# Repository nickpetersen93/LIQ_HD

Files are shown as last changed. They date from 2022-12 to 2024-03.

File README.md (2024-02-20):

# LIQ HD - Lick Instance Quantifier Home cage Device 

## UPDATE: 1/19/2024 (Arduino Mega version only)

We have now included the ability to log the lick data by individual bouts! With this setting turned on, each individual bout will be logged with a line in the file with the side the experimental bottle is on (LEFT or RIGHT), a time stamp, the cage number, which bottle was licked (LEFT or RIGHT), bout lick number, bout lick duration, average lick frequency of that bout, and average inter-lick interval of that bout. Note, this setting will not log the total lick number and lick duration (i.e. licks that do not meet bout criteria).

The "log by bout" setting can be turned on using the GUI under "Parameters to log". This setting can be made the default by changing the Arduino code lines 186-187. For example:

bool log_by_bout = true; 
bool log_by_time = false;
//will set the default to "log by bout".

bool log_by_bout = false; 
bool log_by_time = true;
//will set the default to "log by time" (original logging method).

We have also made it easier to change the bout cutoff time (the amount of time during a drinking bout where an animal stops licking before the bout is considered over) by changing the "bout_cutoff" variable on line 185.

We made some minor changes to the capacitive sensor settings that optimizes the baseline tracking for more consistent lick detection.

------------------------------------------------------------------

## Included in this repository:
  - Arduino code for LIQ HD running off an Arduino Mega
  - Arduino code for LIQ HD running off an Adafruit Grand Central (significantly faster processor speed. NOT FULLY TESTED.)
  - 3D models for all required 3D-printed components in various file formats (STL, STEP, SHAPR)
  - Step-by-step build instructions and video tutorial can be found on the [Wiki page](https://github.com/nickpetersen93/LIQ_HD/wiki/LIQ-HD---Step-by-Step-Tutorial "LIQ HD - Step-by-Step Tutorial")
  
------------------------------------------------------------------

### Required Arduino Libraries:
  - Adafruit_GFX.h
  - RTClib.h
  - SdFat.h
  - Adafruit_MPR121.h
  - Adafruit_ILI9341.h
  - Adafruit_FT6206.h
  
------------------------------------------------------------------

### Publication Link: https://www.eneuro.org/content/10/4/ENEURO.0506-22.2023

## Abstract

Investigation of rodent drinking behavior has provided insight into drivers of thirst, circadian rhythms, anhedonia, and drug and ethanol consumption. Traditional methods of recording fluid intake involve periodically weighing bottles, which is cumbersome and lacks temporal resolution. Several open-source devices have been designed to improve drink monitoring, particularly for two-bottle choice tasks. However, recent designs are limited by the use of infrared photobeam-break sensors and incompatibility with prolonged undisturbed use in ventilated home cages. Beam-break sensors lack accuracy for bout microstructure analysis and are prone to damage from rodents. To address these concerns, we designed LIQ HD (Lick Instance Quantifier Home cage Device) with the goal of utilizing capacitive sensors to increase accuracy and analyze lick microstructure, building a device compatible with ventilated vivarium home cages, increasing scale with prolonged undisturbed recordings, and creating a design that is easy to build and use with an intuitive touchscreen graphical user interface. The system tracks two-bottle choice licking behavior in up to 18 rodent home cages, or 36 single bottles, on a minute-to-minute timescale controlled by a single Arduino microcontroller. The data are logged to a single SD card, allowing for efficient downstream analysis. With sucrose, quinine, and ethanol two-bottle choice tasks, we validated that LIQ HD has superior accuracy compared to beam-break sensors. The system measures preference over time and changes in bout microstructure, with undisturbed recordings lasting up to 7 days. All designs and software are open-source to allow other researchers to build upon the system and adapt LIQ HD to their animal home cages.

<p align="center">

</p>

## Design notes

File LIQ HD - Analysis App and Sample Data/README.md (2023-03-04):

# LIQ HD Analysis 

<p align="center">
LIQ HD Analysis App
</p>

## Included in this folder:
  - LIQ HD Analysis 1.0 Installer for MacOS and Windows
  - Sample LIQ HD Data
    - "LIQ_HD_Sample_Data_Water.CSV" contains data from 16 cages of water two-bottle choice for 1 week. Cages 17 & 18 are empty.
    - "LIQ_HD_Sample_Data_EtOH_Sucrose.CSV" contains data from 8 cages of ethanol two-bottle choice (Cages 1 to 8 - 7% EtOH versus water), and 8 cages of sucrose two-bottle choice (Cages 9 to 16 - 1% Sucrose versus water) for 1 week. Cages 17 & 18 are empty.
  - A How-To Guide can be found on the [Wiki page](https://github.com/nickpetersen93/LIQ_HD/wiki/LIQ-HD-Analysis-App-Guide) (Coming soon!)

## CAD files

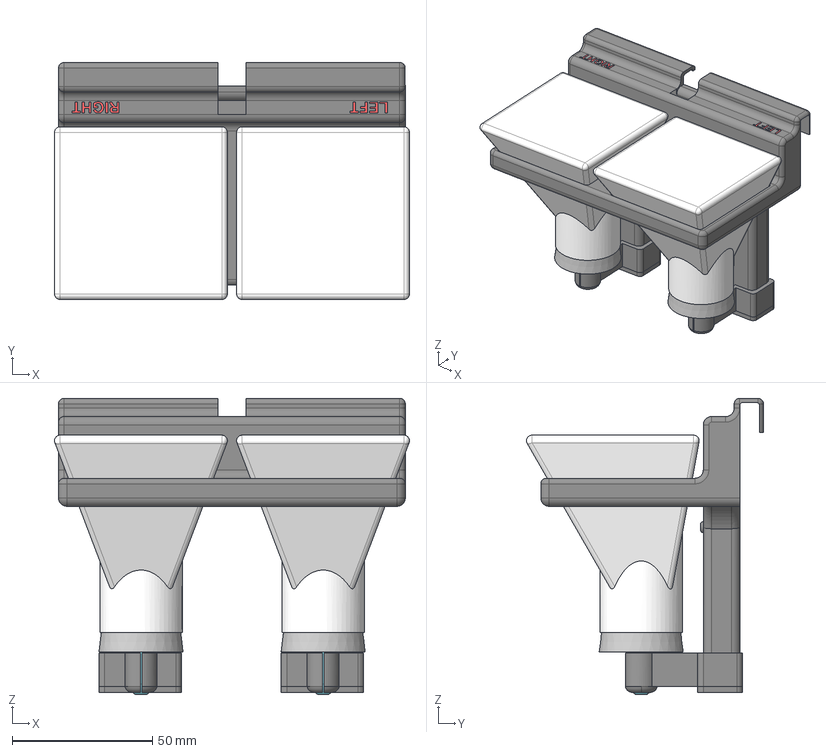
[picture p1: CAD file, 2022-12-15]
LIQ HD - 3D Models github/STEP/LIQ HD - Full model.step
126.5 x 84.5 x 105.6 mm
spouts
stoppers
clips
Text - LEFT/RIGHT
bottles

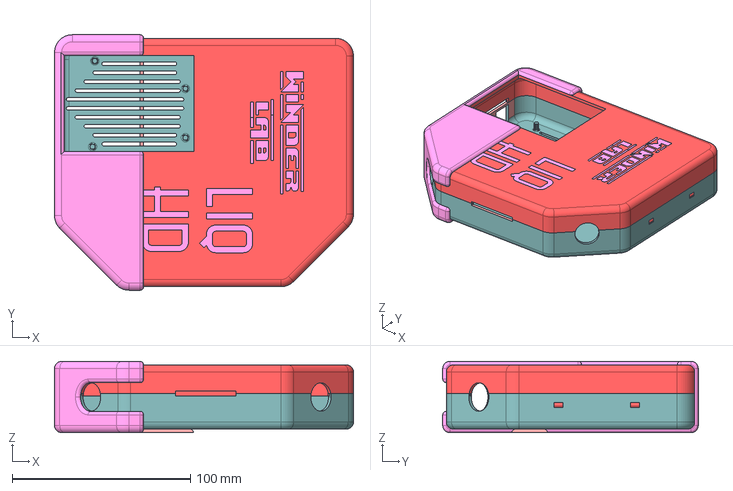
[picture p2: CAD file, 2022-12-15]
LIQ HD - 3D Models github/STEP/LIQ HD - Arduino Box.step
167.8 x 143.4 x 40.0 mm

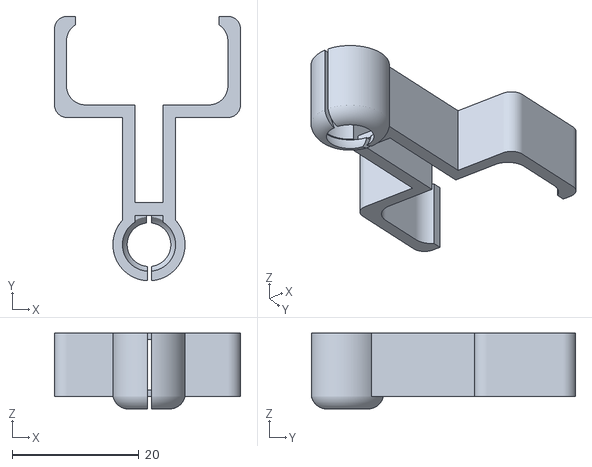
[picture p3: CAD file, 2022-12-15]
LIQ HD - 3D Models github/STL/LIQ HD - Device CLIP 10mm.stl
29.4 x 41.8 x 12.0

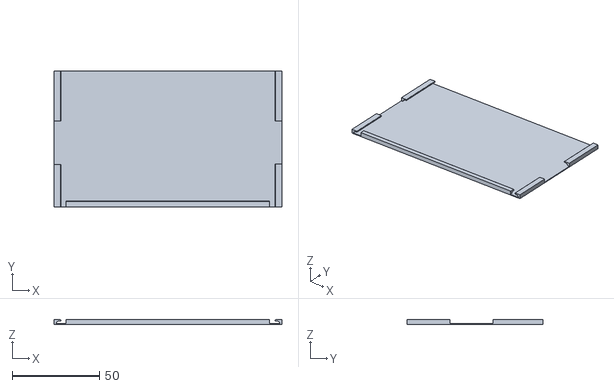
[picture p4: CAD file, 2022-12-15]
LIQ HD - 3D Models github/STL/LIQ HD Card Holder.stl
131.0 x 78.0 x 2.80

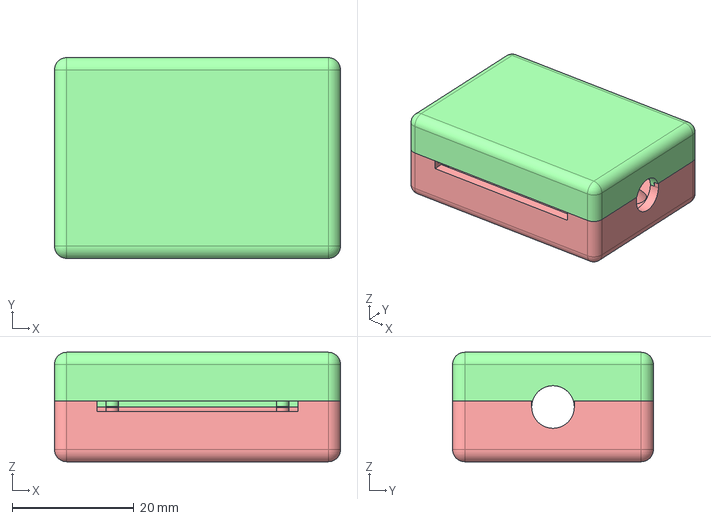
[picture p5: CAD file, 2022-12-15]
LIQ HD - 3D Models github/STEP/LIQ HD - Sensor Box.step
47.0 x 33.0 x 18.0 mm

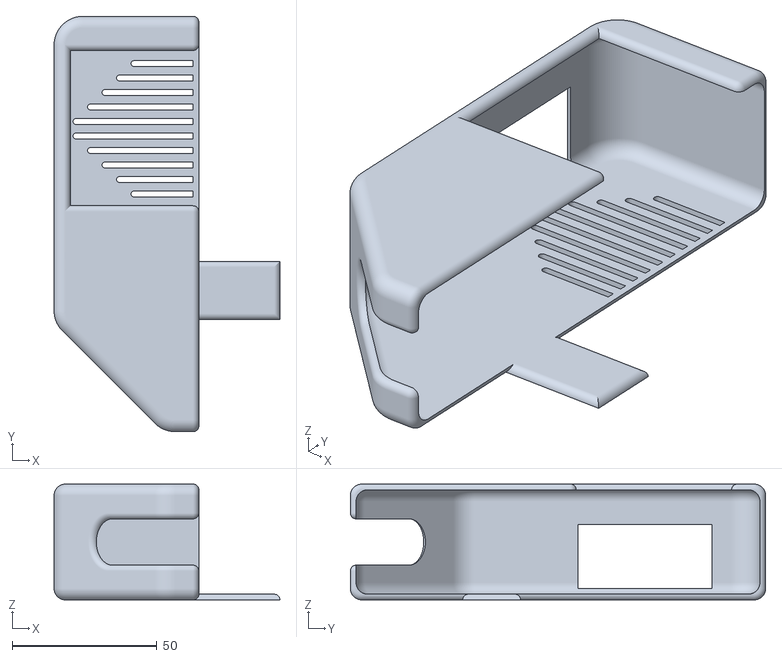
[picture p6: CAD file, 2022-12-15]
LIQ HD - 3D Models github/STL/LIQ HD - Arduino box HOLDER.stl
78.0 x 143.4 x 40.0

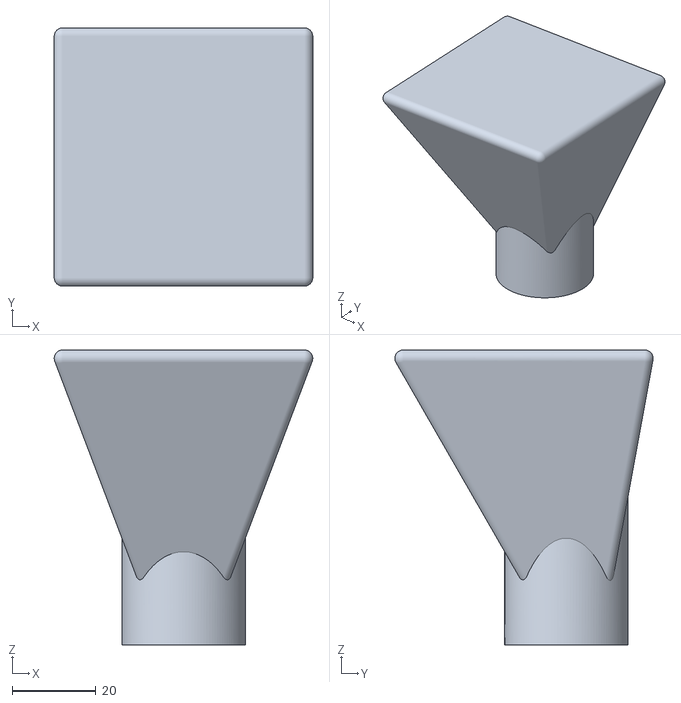
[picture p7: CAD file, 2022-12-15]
LIQ HD - 3D Models github/STL/LIQ HD - Bottle 27mm opening.stl
61.6 x 61.5 x 70.3

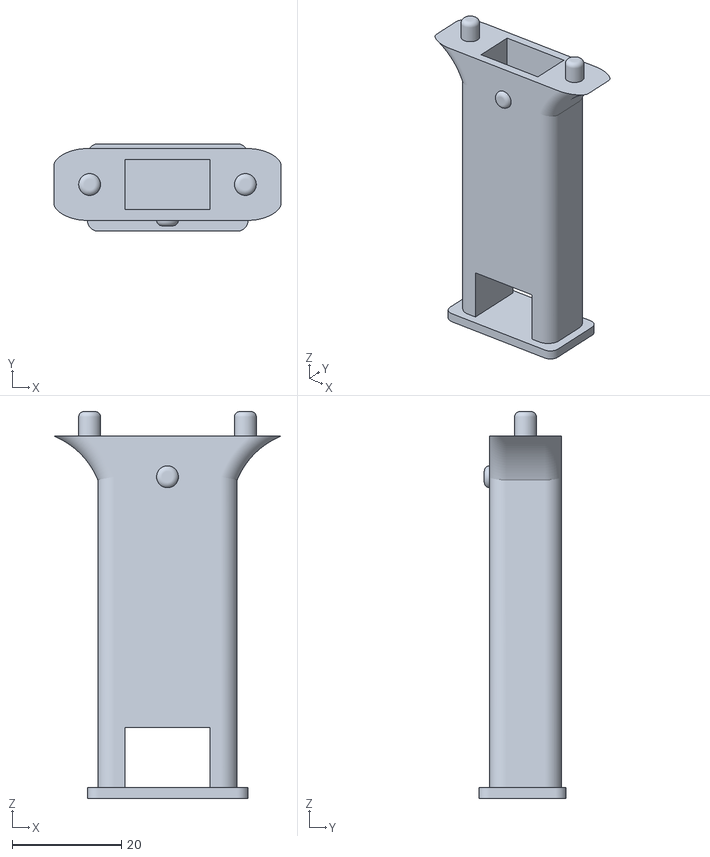
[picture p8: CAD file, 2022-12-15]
LIQ HD - 3D Models github/STL/LIQ HD - Device LEG .stl
41.5 x 16.0 x 70.8

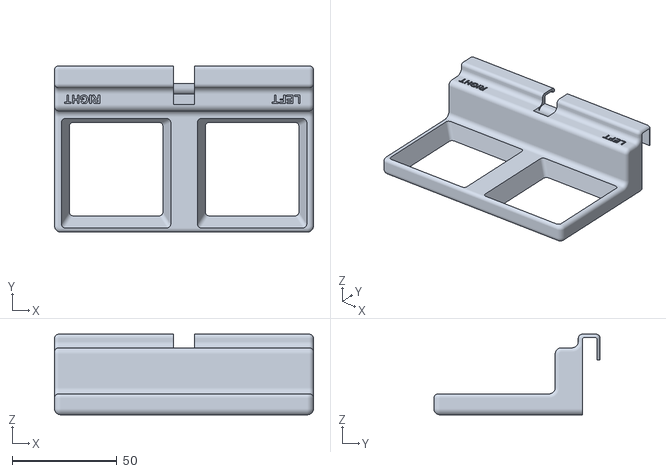
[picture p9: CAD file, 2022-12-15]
LIQ HD - 3D Models github/STL/LIQ HD - Device TOP.stl
123.6 x 79.4 x 38.5

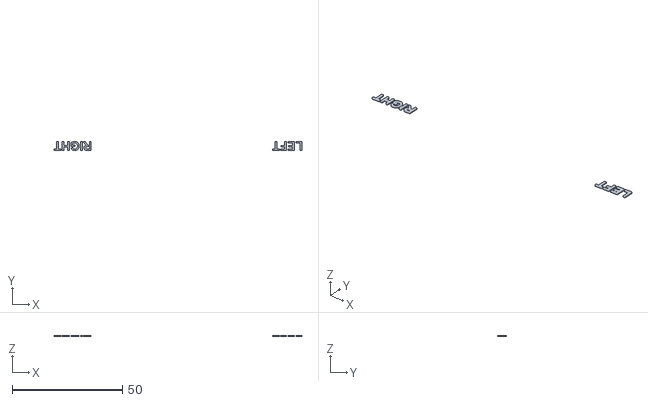
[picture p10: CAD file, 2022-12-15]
LIQ HD - 3D Models github/STL/LIQ HD - Device TEXT.stl
112.5 x 4.14 x 0.6

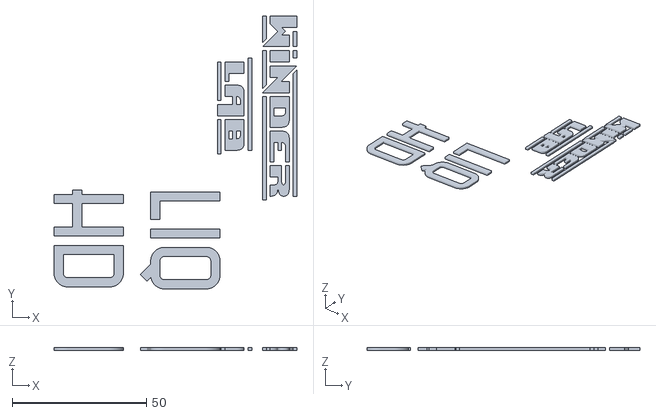
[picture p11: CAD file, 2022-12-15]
LIQ HD - 3D Models github/STL/LIQ HD - Arduino box TEXT.stl
90.5 x 101.6 x 1.00

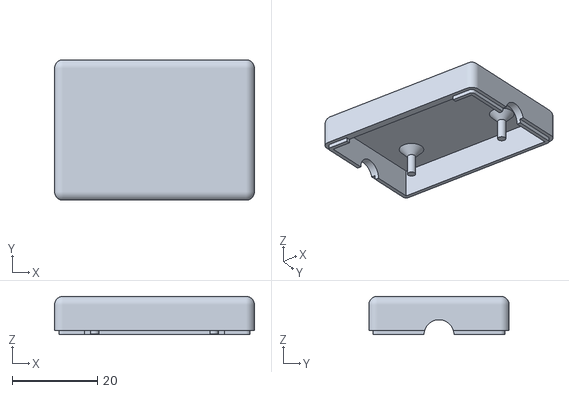
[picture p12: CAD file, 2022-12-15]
LIQ HD - 3D Models github/STL/LIQ HD - Sensor case TOP.stl
47.0 x 33.0 x 9.00

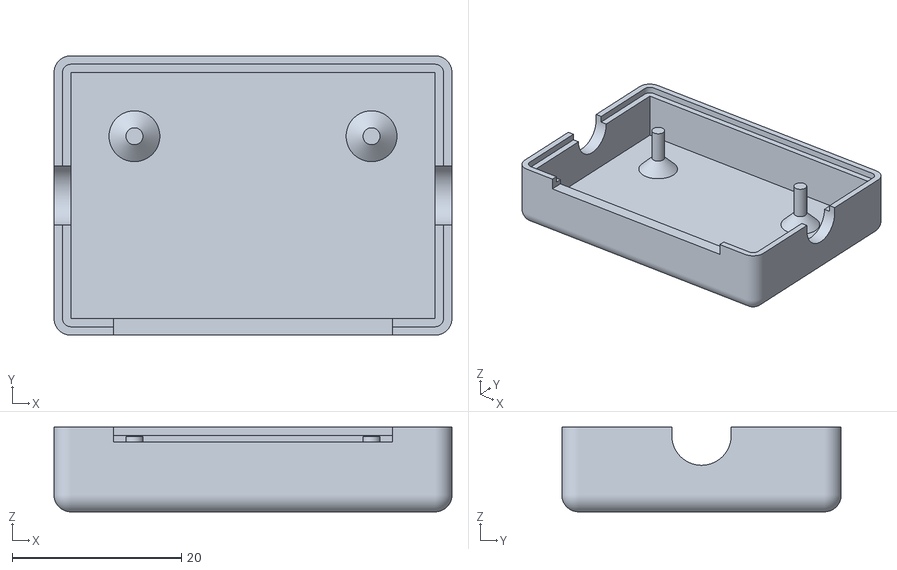
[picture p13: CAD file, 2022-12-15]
LIQ HD - 3D Models github/STL/LIQ HD - Sensor case BOTTOM.stl
47.0 x 33.0 x 10.0

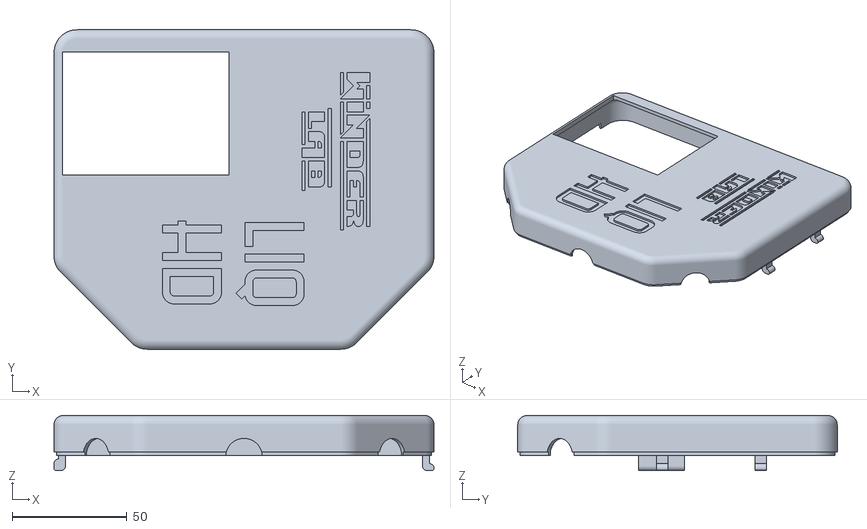
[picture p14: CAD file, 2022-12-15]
LIQ HD - 3D Models github/STL/LIQ HD - Arduino box TOP.stl
165.8 x 139.4 x 24.0

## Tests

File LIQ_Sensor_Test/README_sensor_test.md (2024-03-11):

Upload this script to your LIQ HD system and open the serial plotter on the Arduino IDE to visually test lick threshold settings! It is recomended to test only 2-4 sensors because the serial plotter begins to run slowly. If the serial plotter is running too quickly to visualize detected licks, you can slow it down by adding a delay (change "delay_time"). Run this test on a fully built LIQ system in its experimental environment because certain changes, such as wire length, will affect the necessary threshold settings.

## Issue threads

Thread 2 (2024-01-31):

### ISSUE TITLE
STL Files provided don't match with video

### ISSUE THREAD

**Issue by IamMistborn** [nickpetersen93/LIQ_HD#2]
Hey there, I was going through the tutorial when I realized the Youtube video STL files and the STL files provided on Thingiverse don't match up. What's more, it looks like the STL files have additional hardware that isn't mentioned in the video, Step-By-Step tutorial, or materials list. I'm mostly wondering if I'm missing something crucial that was added later on. Thanks!

**Comment by nickpetersen93** [comment]
Hello! We have not uploaded anything to Thingiverse, but it looks like there is a modified version that was adapted from our system made by another lab [(link)](https://www.thingiverse.com/thing:6301818). From what I can tell from their design, the general build of the electronic components in the same, but with a modified in-cage sipper sensor to fit their cages.

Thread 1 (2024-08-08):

### ISSUE TITLE
Time resolution of data aggregation

### ISSUE THREAD

**Issue by shun4423** [nickpetersen93/LIQ_HD#1]
This system seems to summarize data as licks per minute, but is it possible to summarize data as licks per second?

**Comment by nickpetersen93** [comment]
Theoretically, yes, the code can be modified to log every second, but I don’t think it would be helpful. It takes time to write to the file and save to the SD card, so this would probably cause significant lapses in the lick detection. Is there a specific reason you’d like to log every second? We are currently working on updating the code to include an option to log every drinking bout rather than logging every ‘x’ minutes. This will decrease the file size and also allow for very specific analysis of each bout. We are also fine-tuning the lick detection settings to further increase the accuracy. This should be released in the next few weeks!

**Comment by shun4423** [comment]
Where a licked clump is considered terminated varies. In my case, the end of a bout is when there is no lick for one second after consecutive licks. I also calculate the interval between boats. Therefore, I fear that if I compile the data in one-minute increments, I will not be able to calculate these.

**Comment by Zepieton** [comment]
We have a built a Liq HD system and it seems to work fine so far; but we want to to be able to use each lick bout as a TTL to time-lock them to specific events (brain recordings). Any way to achieve this with the current code? Or is it going to be in the updated code (and is there an estimated ETA?)?. Thank you for your effort!!!

**Comment by nickpetersen93** [comment]
Great to hear you have it up and running! I have just uploaded updated code that will allow you to log each bout. Please note the analysis app does not yet support this file output format. 

Adding a TTL should be relatively easy. I have used an Arduino to send TTLs to our fiber photometry system, so I know it is definitely possible. It will mostly be limited by the number of available pins on the Arduino. Will you be recording from multiple animals at the same time, or just from one LIQ bottle pair? Would you want a TTL for each lick, each bout, or both?

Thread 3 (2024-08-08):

### ISSUE TITLE
Having a few problems, also have a few question

### ISSUE THREAD

**Issue by J-M-Cecil** [nickpetersen93/LIQ_HD#3]
Hey there! I set everything up a slightly modified version of this for my lab but we're having a few problems.

Modifications: 

1) Instead of the provided bottles and 'Device CLIP 10mm' cad part I designed my own part that interfaces with a premade bottle. The interface works in the exact same way.

2) Some minor CAD changes on the cases for cosmetic purposes

3) Some minor cosmetic changes to the code (only messed with the logos that come up)

Problems:
1) The main issue we're having is that the lick count increases on its own during testing. After hitting "Start!", the lick monitoring screen comes up,  and I'll tap/rub opening to a bottle with a wet finger, but I get no response. I hit Refresh and all values stay 0:0. After about a minute however, the values increase by themselves. Typically the first values are around 150:30 (L:R, with right side being experimental). After another minute, the values increase by roughly the same amount. I'm not sure if it's reading the test 'licks' I do or something else entirely.

2) The SD card fails a few minutes into a recording session. I'll plug things in, hit "Start!" and the lick monitoring screen comes up. More often than not, in a couple minutes, the screen dims and a error page pops up that says "SD card failed or not inserted" along with the date and time of the failure.

Questions:
1) What does the hardware actually measure/ what is the computer actually reading? When the mice lick, is there a voltage drop that's measured? Or is there a capacitance change? Mostly just curious on this one.

2) Is there a built in test function somewhere where you get an immediate indication every time a bottle is "licked?"

Thanks for your time.

**Comment by nickpetersen93** [comment]
Hey there,
Happy to see you've made modifications to fit your needs! Are you using mice or rats, and what brand and model of cage are you using? Once you have it up and running smoothy, we would love to be able to share your models with the community!

From the sounds of it, you may be getting "ghost licks" due to the sensor threshold being too low. Given your modifications to the design, the current lick threshold settings may not be appropriate and will likely need adjustment. The default settings are also designed for mice, so the use of rats will definitely require changes to the settings. Also, the way the code is written, it will only update the numbers for the screen every minute (even if you hit refresh). One way to test the detected licks in real time is to physically look at the MPR121 sensor board. There is a small red LED on each board that turns on every time a sensor is touched or released. Using this is useful to quickly check if you are getting ghost licks or if it was just counting your finger taps with the minute delay in the screen. It is also important to note that touching the wires can sometime set off the sensors, so it is important to avoid touching the wires while the system is running.

The sensors measure a change in capacitance, similar to a touch screen on a smart phone. So, touching the sensor with your hand with generate a large change in capacitance, whereas a mouse's tongue will generate a very small change in capacitance. With that said, it is important to test these setting using the actual experimental environment. I just uploaded a code that I use to test sensor settings! Simply upload it to your Arduino of your built LIQ system and open the serial plotter on the Arduino IDE (with the Arduino plugged into your computer). You can then play around with the touch and release thresholds to determine your optimal settings. A lick will be detected with the recorded value goes above the "touch_threshold" and will end the lick when the value goes below the "release_threshold". It is best to keep the release_threshold at about half the value of the touch_threshold.  It can be a bit frustrating to wait for an animal to lick, so we will sometimes take a space cage of mice (group housed) and put 10% sucrose (or something similar) in the bottles to increase the likelihood that the animals will lick. 

As far as your SD card problem, it may be a couple different issues. I'm not sure why, but we have had some SD cards in the past that have given us the same problem and we eventually just replaced those cards with new ones and it fixed the problem. The Arduino will also sometimes malfunction if the lick threshold settings are too low and it is picking up a lot of erratic ghost licks, which may be your issue. I made some minor tweaks to the SD error function with the most recent code update, so I would also try that if you haven't yet. 

Hope this helps!
Nick

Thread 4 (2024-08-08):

### ISSUE TITLE
Minor Errors After Uploading The Code

### ISSUE THREAD

**Issue by EVienneau03** [nickpetersen93/LIQ_HD#4]
Hi there,

The lab i am apart of has decided to switch over to the LIQ HD to gain a more accurate drinking representation of our mice colony. We have also had a hanful of changes to the device top (resized to fir our cages, reinforced some areas and added clips so it does not sag) and leg height.

A few issue that have come up when trying to set up the LIQ HD

1. The SD card said SD Card failed..., I have tried a handful of different cards, not new but have been working and reformatted since their previous use. 

3. The other issue is changing the date and time. It did not sync to my computers date and time, but it has set the date to 72/96/2095 and the time to 72:00. When i try to change the date and time, the device will not accept my changes as i clear the time, enter the new number and confirm it with ok and it will disregard my changes that i attempted to make. Nor will it change when i hit save. All other changable setting are wokring perfectly fine!

If you have any advice on how to fix both the sd card issue and the date and time issue?

Best,
Evan V.
Emmanuel College, Crofton Lab Assistant

**Comment by nickpetersen93** [comment]
Hey Evan,

The most likely a hardware issue with the data logger shield, which also includes the real-time clock. Take a close look at the data logger - Is the "CS" solder pad connection cut? Was a jumper wire connected from pin 7 to the "CS" pin? Are any of the pins accidentally bridged together with solder? Were any PCB tracks (conductive paths used to connect each point on the board) damaged during the soldering process? If everything looks correct, the board itself may be faulty and you may want to try a different data logger.

Hope this helps! Feel free to reach out if you're still having problems.

Nick

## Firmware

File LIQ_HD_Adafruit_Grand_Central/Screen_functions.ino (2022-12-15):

//==========================================================================================

void start_display()
{
  tft.begin();
  if (!ts.begin()) {
    DEBUG_PRINTLN("Couldn't start touchscreen controller");
    while (1);
  }
  DEBUG_PRINTLN("Touchscreen started");
}

//==========================================================================================

void WelcomeScreen() //work on this with new name and logo design
{
  tft.setRotation(2);
  tft.fillScreen(ILI9341_BLACK);
  drawBitmap(0, 60, welcome_logo, 240, 173, ILI9341_WHITE);
  wait(2000);
}

//==========================================================================================

void set_brightness()
{
  // fetch the time
  hour_now = now.hour();

  if (lights_on < lights_off) {
    if (hour_now >= lights_on && hour_now < lights_off) {
      analogWrite(5, 255);
    }
    if (hour_now < lights_on || hour_now >= lights_off) {
      analogWrite(5, 10);
    }
  }

  if (lights_on > lights_off) {
    if (hour_now >= lights_on || hour_now < lights_off) {
      analogWrite(5, 255);
    }
    if (hour_now < lights_on && hour_now >= lights_off) {
      analogWrite(5, 10);
    }
  }
}

//======================================================================================

void NickText(String text, int x, int y, int size)
{
  tft.setTextSize(size);
  tft.setCursor(x, y);
  tft.print(text);
}

//======================================================================================

void NickText(int w, int x, int y, int size)
{
  tft.setTextSize(size);
  tft.setCursor(x, y);
  tft.print(w);
}

//======================================================================================

void NickText_center(String text, int center_x, int center_y, int size)
{
  tft.setTextSize(size);
  int16_t x1; int16_t y1; uint16_t w; uint16_t h;
  tft.getTextBounds(text, 0, 320, &x1, &y1, &w, &h);
  int xx = (center_x - 1) - (w / 2);
  int yy = (center_y - 1) + (h / 2);
  tft.setCursor(xx, yy);
  tft.print(text);
}

//======================================================================================

void NickText_center(int variable, int center_x, int center_y, int size)
{
  tft.setTextSize(size);
  int16_t x1; int16_t y1; uint16_t w; uint16_t h;
  String text = String(variable);
  tft.getTextBounds(text, 0, 320, &x1, &y1, &w, &h);
  int xx = (center_x - 1) - (w / 2);
  int yy = (center_y - 1) + (h / 2);
  tft.setCursor(xx, yy);
  tft.print(variable);
}

//==========================================================================================

void Button_center(int center_x, int center_y, int sizeX, int sizeY, uint16_t button_color, uint16_t border_color, uint16_t text_color, String text, int textsize)
{
  int16_t x = center_x - (sizeX / 2);
  int16_t y = center_y - (sizeY / 2);
  tft.fillRoundRect(x, y, sizeX, sizeY, 4, button_color);
  tft.drawRoundRect(x, y, sizeX, sizeY, 4, border_color);
  int16_t x1; int16_t y1; uint16_t w; uint16_t h;
  tft.getTextBounds(text, 0, 320, &x1, &y1, &w, &h);
  int xx = (center_x - 1) - (w / 2);
  int yy = (center_y - 1) + (h / 2);
  tft.setTextColor(text_color);
  tft.setTextSize(textsize);
  tft.setCursor(xx, yy);
  tft.print(text);

  int x_min; int x_max; int y_min; int y_max;
  x_min = x;
  x_max = x + sizeX;
  y_min = y;
  y_max = y + sizeY;
  DEBUG_PRINTLN();
  DEBUG_PRINT(text);
  DEBUG_PRINT(" button borders: p.x>");
  DEBUG_PRINT(x_min);
  DEBUG_PRINT(" && p.x<");
  DEBUG_PRINT(x_max);
  DEBUG_PRINT(" && p.y>");
  DEBUG_PRINT(y_min);
  DEBUG_PRINT(" && p.y<");
  DEBUG_PRINT(y_max);
  DEBUG_PRINT("");
}

//==========================================================================================

void Button_center(int center_x, int center_y, int sizeX, int sizeY, uint16_t button_color, uint16_t border_color, uint16_t text_color, int text, int textsize)
{
  int16_t x = center_x - (sizeX / 2);
  int16_t y = center_y - (sizeY / 2);
  tft.fillRoundRect(x, y, sizeX, sizeY, 4, button_color);
  tft.drawRoundRect(x, y, sizeX, sizeY, 4, border_color);
  int16_t x1; int16_t y1; uint16_t w; uint16_t h;
  tft.getTextBounds(String(text), 0, 320, &x1, &y1, &w, &h);
  int xx = (center_x - 1) - (w / 2);
  int yy = (center_y - 1) + (h / 2);
  tft.setTextColor(text_color);
  tft.setTextSize(textsize);
  tft.setCursor(xx, yy);
  tft.print(text);

  int x_min; int x_max; int y_min; int y_max;
  x_min = x;
  x_max = x + sizeX;
  y_min = y;
  y_max = y + sizeY;
  DEBUG_PRINTLN();
  DEBUG_PRINT(text);
  DEBUG_PRINT(" button borders: p.x>");
  DEBUG_PRINT(x_min);
  DEBUG_PRINT(" && p.x<");
  DEBUG_PRINT(x_max);
  DEBUG_PRINT(" && p.y>");
  DEBUG_PRINT(y_min);
  DEBUG_PRINT(" && p.y<");
  DEBUG_PRINT(y_max);
  DEBUG_PRINT("");
}

//==========================================================================================

void Button(int x, int y, int sizeX, int sizeY, int rad, uint16_t color)
{
  tft.fillRoundRect(x, y, sizeX, sizeY, rad, color);
  tft.drawRoundRect(x, y, sizeX, sizeY, rad, ILI9341_BLACK);
}

//======================================================================================

void error(String str)
{
  show_time = true;
  display_time();
  tft.fillRect(0, 20, 240, 320, ILI9341_RED);
  DEBUG_PRINT("error: ");
  DEBUG_PRINTLN(str);
  tft.setFont();
  tft.setTextWrap(true);
  tft.setFont(&FreeSans9pt7b);
  NickText(str, 5, 50, 1);
  Button_center(120, 250, 220, 60, ILI9341_BLACK, ILI9341_BLACK, ILI9341_WHITE, "Return to Main Menu", 1);
}

//======================================================================================

void display_licks()
{
  tft.setFont(&FreeSans9pt7b);
  tft.fillRect(0, 20, 240, 222, ILI9341_RED);
  NickText_center("Total lick number", 100, 32, 1);
  NickText_center("for each cage (L-R)", 105, 51, 1);
  tft.setFont();
  Button_center(215, 56, 45, 20, ILI9341_BLACK, ILI9341_BLACK, ILI9341_WHITE, "", 1); //refresh button
  NickText_center("Refresh", 217, 49, 1);

  int spacing = 20;
  int x1 = 4;
  int x2 = 120;
  int y1 = 80;
  int y2 = y1 + spacing;
  int y3 = y2 + spacing;
  int y4 = y3 + spacing;
  int y5 = y4 + spacing;
  int y6 = y5 + spacing;
  int y7 = y6 + spacing;
  int y8 = y7 + spacing;
  int y9 = y8 + spacing;

  tft.setFont(&FreeSans9pt7b);
  NickText(F("1"), x1, y1, 0);
  tft.print(F("-"));
  tft.print(total_LN[0]);
  tft.print(F(":"));
  tft.print(total_LN[1]);

  NickText(F("2"), x1, y2, 0);
  tft.print(F("-"));
  tft.print(total_LN[2]);
  tft.print(F(":"));
  tft.print(total_LN[3]);

  NickText(F("3"), x1, y3, 0);
  tft.print(F("-"));
  tft.print(total_LN[4]);
  tft.print(F(":"));
  tft.print(total_LN[5]);

  NickText(F("4"), x1, y4, 0);
  tft.print(F("-"));
  tft.print(total_LN[6]);
  tft.print(F(":"));
  tft.print(total_LN[7]);

  NickText(F("5"), x1, y5, 0);
  tft.print(F("-"));
  tft.print(total_LN[8]);
  tft.print(F(":"));
  tft.print(total_LN[9]);

  NickText(F("6"), x1, y6, 0);
  tft.print(F("-"));
  tft.print(total_LN[10]);
  tft.print(F(":"));
  tft.print(total_LN[11]);

  NickText(F("7"), x1, y7, 0);
  tft.print(F("-"));
  tft.print(total_LN[12]);
  tft.print(F(":"));
  tft.print(total_LN[13]);

  NickText(F("8"), x1, y8, 0);
  tft.print(F("-"));
  tft.print(total_LN[14]);
  tft.print(F(":"));
  tft.print(total_LN[15]);

  NickText(F("9"), x1, y9, 0);
  tft.print(F("-"));
  tft.print(total_LN[16]);
  tft.print(F(":"));
  tft.print(total_LN[17]);

  NickText(F("10"), x2, y1, 0);
  tft.print(F("-"));
  tft.print(total_LN[18]);
  tft.print(F(":"));
  tft.print(total_LN[19]);

  NickText(F("11"), x2, y2, 0);
  tft.print(F("-"));
  tft.print(total_LN[20]);
  tft.print(F(":"));
  tft.print(total_LN[21]);

  NickText(F("12"), x2, y3, 0);
  tft.print(F("-"));
  tft.print(total_LN[22]);
  tft.print(F(":"));
  tft.print(total_LN[23]);

  NickText(F("13"), x2, y4, 0);
  tft.print(F("-"));
  tft.print(total_LN[24]);
  tft.print(F(":"));
  tft.print(total_LN[25]);

  NickText(F("14"), x2, y5, 0);
  tft.print(F("-"));
  tft.print(total_LN[26]);
  tft.print(F(":"));
  tft.print(total_LN[27]);

  NickText(F("15"), x2, y6, 0);
  tft.print(F("-"));
  tft.print(total_LN[28]);
  tft.print(F(":"));
  tft.print(total_LN[29]);

  NickText(F("16"), x2, y7, 0);
  tft.print(F("-"));
  tft.print(total_LN[30]);
  tft.print(F(":"));
  tft.print(total_LN[31]);

  NickText(F("17"), x2, y8, 0);
  tft.print(F("-"));
  tft.print(total_LN[32]);
  tft.print(F(":"));
  tft.print(total_LN[33]);

  NickText(F("18"), x2, y9, 0);
  tft.print(F("-"));
  tft.print(total_LN[34]);
  tft.print(F(":"));
  tft.print(total_LN[35]);
}

//==========================================================================================

void display_time()
{
  if (show_time) {
    show_time = false;

    DateTime now = rtc.now();
    min_now = now.minute();
    tft.setFont(&FreeSansBold9pt7b);
    tft.setTextSize(1);
    tft.fillRect(0, 0, 240, 20, ILI9341_BLACK);
    tft.setCursor(0, 14);
    tft.setTextColor(ILI9341_WHITE, ILI9341_BLACK);
    tft.print(now.month());
    tft.print("/");
    tft.print(now.day());
    tft.print("/");
    tft.print(now.year());
    tft.setCursor(190, 14);
    tft.print(now.hour());
    tft.print(":");
    if (now.minute() < 10) {
      tft.print("0");
    }
    tft.print(now.minute());
  }

  now = rtc.now();
  if (min_now != now.minute()) {
    show_time = true;  //refresh page every minute
  }
}


//==========================================================================================

void drawBitmap(int16_t x, int16_t y, const uint8_t *bitmap, int16_t w, int16_t h, uint16_t color) {
  int16_t i, j, byteWidth = (w + 7) / 8;
  uint8_t byte;
  for (j = 0; j < h; j++) {
    for (i = 0; i < w; i++) {
      if (i & 7) byte <<= 1;
      else      byte   = pgm_read_byte(bitmap + j * byteWidth + i / 8);
      if (byte & 0x80) tft.drawPixel(x + i, y + j, color);
    }
  }
}

//======================================================================================
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

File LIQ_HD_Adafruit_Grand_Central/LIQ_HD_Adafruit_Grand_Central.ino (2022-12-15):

#include "RTClib.h"
#include <Adafruit_GFX.h>
#include <SPI.h>
#include <Wire.h>
#include <SD.h>
#include "SdFat.h"
#include <Adafruit_MPR121.h>
#include <Adafruit_ILI9341.h>
#include <Adafruit_FT6206.h>
#include <math.h>
#include <Fonts/FreeSans9pt7b.h>
#include <Fonts/FreeSans12pt7b.h>
#include <Fonts/FreeSans18pt7b.h>
#include <Fonts/FreeSansBold9pt7b.h>
#include <Fonts/FreeSansBold12pt7b.h>
#include <Fonts/FreeSansBold18pt7b.h>
#include <Fonts/FreeSansBold24pt7b.h>


#define DEBUG //uncomment to turn on debug mode, prints info to Serial Monitor 

#ifdef DEBUG
#define DEBUG_PRINT(x)     Serial.print (x)
#define DEBUG_PRINTDEC(x)     Serial.print (x, DEC)
#define DEBUG_PRINTLN(x)  Serial.println (x)
#else
#define DEBUG_PRINT(x)
#define DEBUG_PRINTDEC(x)
#define DEBUG_PRINTLN(x)
#endif

// The FT6206 uses hardware I2C on the shield
Adafruit_FT6206 ts = Adafruit_FT6206();

// The display also uses hardware SPI, plus #9 & #10
#define TFT_CS 10
#define TFT_DC 9
Adafruit_ILI9341 tft = Adafruit_ILI9341(TFT_CS, TFT_DC);

RTC_PCF8523 rtc; // define the Real Time Clock object
const int chipSelect = SDCARD_SS_PIN; // for the data logging shield, changed from digital pin 10
#define redLEDpin 13
DateTime now;

//capacitive touch device
#ifndef _BV
#define _BV(bit) (1 << (bit))
#endif

// You can have up to 4 on one i2c bus but one is enough for testing!
Adafruit_MPR121 cap = Adafruit_MPR121();
Adafruit_MPR121 cap2 = Adafruit_MPR121();
Adafruit_MPR121 cap3 = Adafruit_MPR121();

// Keeps track of the last pins touched so we know when buttons are 'released'
uint16_t lasttouched1 = 0;
uint16_t currtouched1 = 0;
uint16_t lasttouched2 = 0;
uint16_t currtouched2 = 0;
uint16_t lasttouched3 = 0;
uint16_t currtouched3 = 0;

File logfile; // the logging file
char filename[] = "00000000.CSV";

TS_Point p;
extern uint8_t welcome_logo[];
extern uint8_t main_logo[];
extern uint8_t settings_icon[];
extern uint8_t settings_icon2[];
String E_side = "RIGHT";
String display_page = "main";
bool show_time = true;
bool eject_button;
int LOG_COUNTER;
int SYNC_COUNTER;
unsigned long currentMillis;
unsigned long previousMillis;
int syncTime;
int min_now;
int prev_min;
int curr_min;
int hour_now;
bool refresh_page = true;
int timeouts = 0;
bool ok;
int default_lights_on;
int default_lights_off;
int default_touch_threshold;
int default_release_threshold;
int default_LOG_INTERVAL;
int dafault_SYNC_INTERVAL;
bool default_auto_cal;
int default_auto_cal_time;
int default_auto_cal_sec_since_last_lick;
bool auto_cal_flag = true;
unsigned long cal_timer;
String logging[6];
bool log_LN = true;
bool log_LD = true;
bool log_BN = true;
bool log_BD = true;
bool log_BLN = true;
bool log_BLD = true;

//enough for 18 cages, 2 lickometers per cage
unsigned long LickDuration[36];
unsigned long LickNumber[36];
unsigned long BoutNumber[36];
unsigned long BoutDuration[36];
unsigned long BoutLickNumber[36];
unsigned long BoutLickDuration[36];
unsigned long Elapsedtime[36];
unsigned long total_LN[36];
int lick_bout_countdown[36];
unsigned long bout_timer[36];
unsigned long bout_start_timer[36];
bool in_bout[36];
bool licking[36];
unsigned long time_now[36];


// how many minutes between grabbing data and logging it.
int LOG_INTERVAL = 1; // IN MINUTES! between entries (reduce to take more/faster data)
// how many milliseconds before writing the logged data permanently to disk
int SYNC_INTERVAL = 10; // IN MINUTES! between calls to flush() - to write data to the card
unsigned long emergency_counter = 60050; //1 minute +50ms

// Typically touch threshold > release threshold for debouncing
// Decrease value to increase sensitivity
int touch_threshold = 2; //default = 12
int release_threshold = 0; //default = 6
bool auto_cal = false;
int auto_cal_time = 7;
int auto_cal_sec_since_last_lick = 60;

int lights_on = 6; //time of day (24hr time) housing lights turn ON
int lights_off = 18; //time of day (24hr time) houseing lights turn OFF

//==========================================================================================

void setup() {

  Serial.begin(115200);
  wait(500);

  pinMode(chipSelect, OUTPUT);
  pinMode(5, OUTPUT); // set screen brightness pin as output
  analogWrite(5, 255);

  set_defaults(); //save coded settings as the default settings

  start_display(); //initialize display

  start_rtc(); //iniitialize rtc

  WelcomeScreen(); //display welcome screen at startup

  set_brightness(); //set screen brightness depending on light cycle

}

//==========================================================================================

void loop() {

  main_menu_page();

  recording_page();

  pause_page();

  SD_error_page();

  settings_page();

}
